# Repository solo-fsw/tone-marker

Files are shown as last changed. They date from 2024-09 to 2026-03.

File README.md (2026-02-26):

# Tone Marker

## Introduction
The purpose of the "Tone Marker" device is to translate high-frequency tones ($\ge$ 15 kHz) into Transistor-transistor Logic (TTL) markers. This allows any application with an audio output (e.g. virtual reality games, websites, cellphones) to send custom markers (values ranging from 0 up to 255) by embedding these marker tones in the audio output. The tones are filtered out and not audible to the participants.

Sending markers is necessary for synchronization of recorded data (e.g. BIOPAC measurements) with VR experiences, where hardware control is not possible. Marker tones are chosen in such a way that they are inaudible for the participant (through audio filtering).

The Tone Marker device is shown below. Note that the circles above the D7 to D0 label are LEDS indicating the currently active marker.

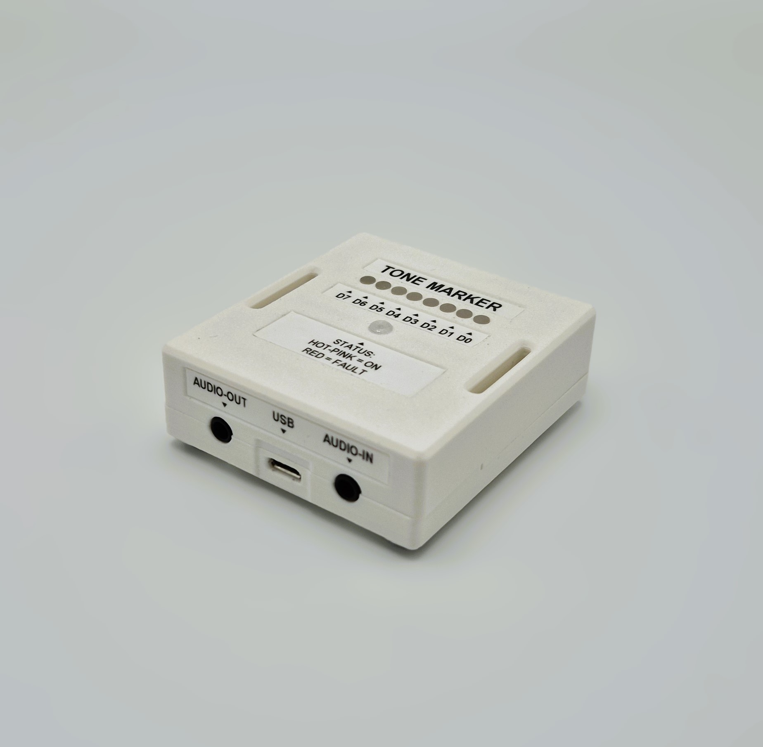
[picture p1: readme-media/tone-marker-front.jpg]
The Tone Marker device

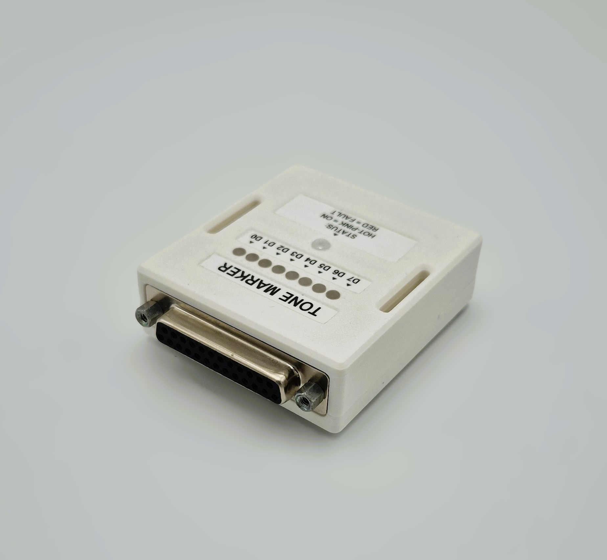
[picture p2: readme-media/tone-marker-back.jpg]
The Tone Marker device


## How to use it in your project?

1. Open your original audio or video file in editing software such as Audacity or Adobe Premiere Pro.
2. Download the audio files from the `media` folder. Both MP3 and WAV formats are available — choose the format that best fits your project requirements.
3. Create a new audio track in your editing software, and place the tone markers at the exact timestamps where you want to trigger events or synchronize actions.
4. Make sure that the marker track aligns correctly with the original audio.
5. Export the final project with both audio tracks included, so the tone markers can overlap with the original audio.

## How was Tone Marker device implemented?

### Setup
The Tone Marker device consists of a [Teensy 4.0](https://www.pjrc.com/store/teensy40.html) soldered to a custom PCB, which is based on the [Teensy Audio Shield](https://www.pjrc.com/store/teensy3_audio.html).
Power is provided through a Mini-USB connection to a dedicated power source (such as a powerbank). The audio input (from e.g. the VR glasses) is fed into the tone-marker, while simultaneously being fed directly into the marker destination (as a backup). Marker output is done through a Female DB25 connector, which is then connected to the required data recording device (e.g. BIOPAC, BIOSEMI).

An overview of the internal and external connections is shown below.

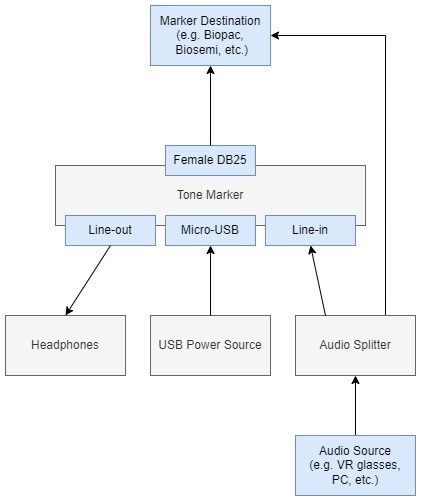
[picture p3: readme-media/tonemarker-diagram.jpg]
An overview of the connection in / to the Tone Marker device


> **NOTE**: Do not disconnect the Tone Marker device from power while it is still connected to a powered marker destination (e.g. a BIOPAC that is turned on). This may cause the Tone Marker device to enter a state where it attempts to power itself by drawing power from the marker destination, which may cause damage to the Teensy or the marker destination device. In this undesired state, the Tone Marker device's status LED may glow red instead of hot-pink.

### Communication protocol

The device expects tones (or combinations of tones) of specific frequencies. The device is currently uses an encoding system with a signal line and two data lines. The signal line makes the device enter listening mode. In listening mode the device receives a bitstring by interpreting the other two frequencies as either 0's (LOW) or 1's (high).

Frequencies are detected by the Goertzel algorithm, and are therefore optimized for their respective Goertzel bin. This is done for the Goertzel algorithm using 150 clock cycles and a sampling frequency of 44100, resulting in the following frequencies:

- **Signal frequency**: 15288.0 Hz
- **Data LOW frequency**: 15582.0 Hz
- **Data HIGH frequency**: 15876.0 Hz

### Delay

Due to time needed for communication and calculation of markers, there is a delay between the onset of the marker tones and the detection of a marker by a marker recipient (such as a Biopac). This delay is approximately $1668$ ms, with a standard deviation of $5.66$ ms.

## Known Issues

### Transient Marker Values
It was noticed that when measuring the marker outputs at 25 kHz using a BIOPAC, approximately 24 of 344 markers showed intermediate values when setting all bits to their ON state (255). When measuring at 2 kHz, the same problem occurred only once (1 / 344). In all cases, the intermediate values had a duration of only a single sample.

As such, it is vitally important to find and remove any such intermediate values before analyzing the data. Please not that the [PhysioData Toolbox](https://physiodatatoolbox.leidenuniv.nl/) automatically corrects for this by removing single-sample markers.

Note, it was not ruled out that this issue was (partly) caused by the BIOPAC's possibly non-simultaneous sampling of the digital input ports.

### Single-Register Patch
The current design spreads the marker IO pins across multiple port registers on the Teensy. A possible fix would be to redesigned the PCB in such a way that it makes use of a single port register, allowing faster bit setting. This may be accomplished using the pins mentioned below, since they are not used by the teensy audio shield, and can all be controlled by changing the GPIO6 register.

| Pin number 	| GPIO6 register index 	|
|------------	|----------------------	|
| 01         	| 02                   	|
| 00         	| 03                   	|
| 24         	| 12                   	|
| 14         	| 18                   	|
| 17         	| 22                   	|
| 16         	| 23                   	|
| 22         	| 24                   	|
| 26         	| 30                   	|

This single-register design was tested and still resulted in 2 out of 360 marker having intermediate values when measured using a BIOPAC at 25 kHz.

### Power supply
Currently, the device enters an undefined state while being connected to the powered BIOPAC without being powered by the micro-USB connector. This is due to the BIOPAC's pull-up resistors and could possibly damage the Teensy. Having the Tone Marker device off and connected to a powered BIOPAC should always be avoided.

## Notes

### Power supply

Some USB power adapters have some noise, which is then audible in the audio signal. In order to avoid this, the usage of a powerbank for powering the Tone Marker device is recommended.

### Volume

Different values of input audio volume might affect Tone Marker performance in different ways. The currently recommended volume level is 65% (on a windows PC) or 80% (on VR glasses).

Furthermore, VR glasses seem to have a lower volume output, so heightening the gain of the marker soundfiles is recommended. Marker functionality can be monitored by checking the green LEDs.

### Additional information / sources

- [Information on the Teensy 4.0 audioshield](https://forum.pjrc.com/index.php?threads/available-teensy-4-0-pins-when-audio-shield-d-attached.58331/)
- [Information on available Teensy pins while the audioshield is connected (and register mappings)](https://github.com/luni64/TeensyTimerTool/wiki/Avoid-PWM-timer-clashes)
- [Teensy pin-register forum thread](https://forum.pjrc.com/index.php?threads/teensy-4-1-digital-i-o-pin-map.64226/)
- [Using Teensy GPIO registers](https://forum.pjrc.com/index.php?threads/tutorial-on-digital-i-o-atmega-pin-port-ddr-d-b-registers-vs-arm-gpio_pdir-_pdor.17532/)
- [DigitalRead, DigitalWrite, DigitalWriteFast speeds](https://forum.pjrc.com/index.php?threads/speed-of-digitalread-and-digitalwrite-with-teensy3-0.24573/)
- [Additional explanation on registers](https://forum.pjrc.com/index.php?threads/unclear-on-how-to-use-ddrx-and-portx-teensy-3-2.53950/)
- [Goertzel Algorithm](https://courses.cs.washington.edu/courses/cse466/11au/resources/GoertzelAlgorithmEETimes.pdf)
- [Changing soundfile audio volume in python](https://stackoverflow.com/questions/43679631/python-how-to-change-audio-volume)

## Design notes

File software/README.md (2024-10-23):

# Software
This directory contains arduino software, that runs on the Teensy-based device, and python code, that is used to generate the marker tones.

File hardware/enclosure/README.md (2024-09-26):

# Enclosure #
Enclosure printed from PLA, see 3mf file.

Parts:
 - Bit LEDs light pipes: [LFB025CTP VCC](https://nl.rs-online.com/web/p/led-light-pipes/1371421).
 - Jackscrews: [RS PRO Screw Lock For Use With D Connector](https://nl.rs-online.com/web/p/d-sub-connector-accessories/0814039).
 - Threaded inserts: [RS PRO, M3 Brass Threaded Insert](https://nl.rs-online.com/web/p/threaded-inserts/0278534?gb=s)

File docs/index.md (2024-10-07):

# Tone Marker Test

## Standard encoding testfile

https://github.com/user-attachments/assets/777e4f00-1f3a-4553-8680-ae20917f563c

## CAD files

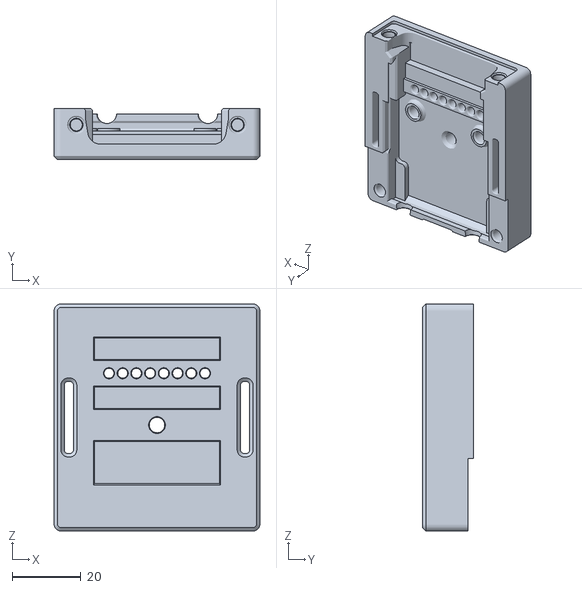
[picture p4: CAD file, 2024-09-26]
hardware/enclosure/Tone Marker v2 v26_Tone Marker v2 v26_Base_1_Body2.stl
60.0 x 15.0 x 66.2

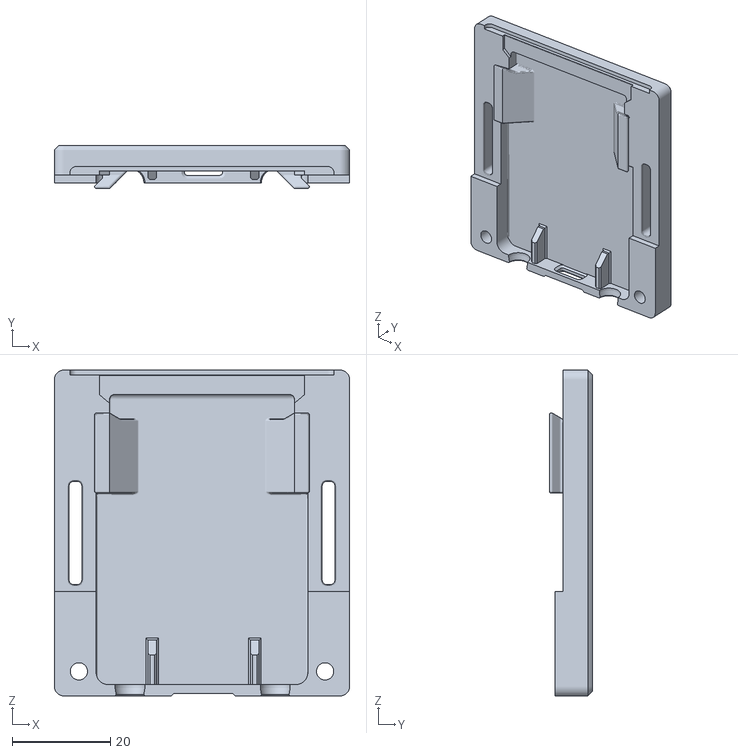
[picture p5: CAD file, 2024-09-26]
hardware/enclosure/Tone Marker v2 v26_Tone Marker v2 v26_Lid_1_Body1.stl
60.0 x 8.82 x 66.2

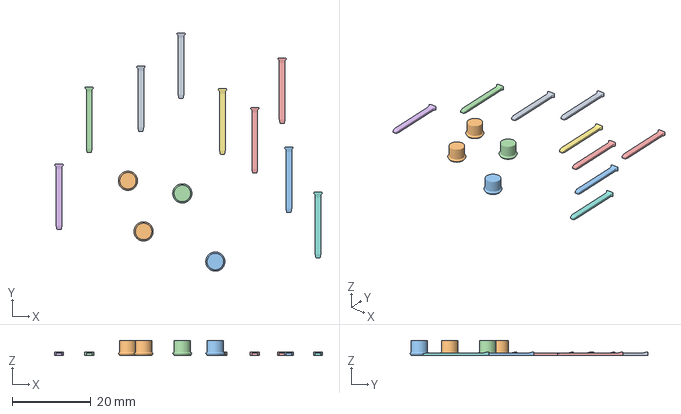
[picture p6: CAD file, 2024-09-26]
hardware/enclosure/LightPipes.3mf
68.1 x 60.6 x 3.87 mm
Body1.stl x 9
Component32.stl x 4

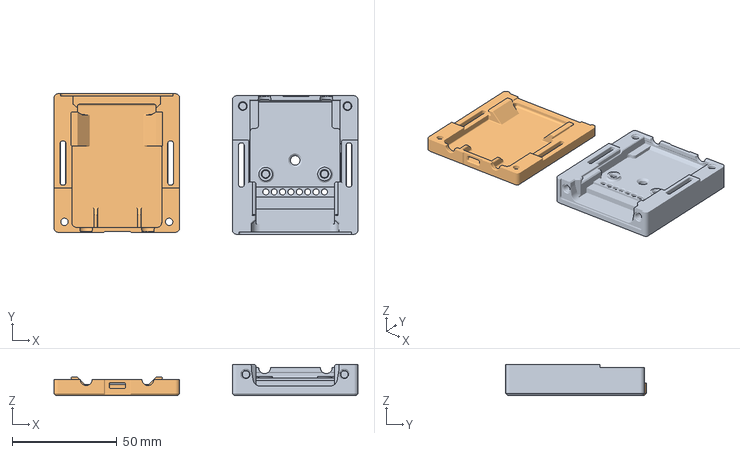
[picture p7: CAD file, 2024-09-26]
hardware/enclosure/Tone Marker.3mf
145.2 x 67.1 x 15.0 mm
Tone Marker v2 v26_Tone Marker v2 v26_Base_1_Body2.stl
Tone Marker v2 v26_Tone Marker v2 v26_Lid_1_Body1.stl

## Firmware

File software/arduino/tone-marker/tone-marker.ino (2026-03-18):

#include <Audio.h>
#include <Wire.h>
#include <SPI.h>
#include <SerialFlash.h>
#include <FastLED.h>

#define REQUIREMENTS_FOLLOWED false

#define DATA_PIN 17
#define N_LEDS 1
#define STRIPS 1
#define N_BITS 3
#define N_UNUSED_BITS 5

// Tool: https://www.pjrc.com/teensy/gui/

// GUItool: begin automatically generated code
AudioInputI2S i2s1;                  //xy=101,321
AudioFilterBiquad filterMarker;      //xy=346,417
AudioMixer4 mixerLeft;               //xy=348,268
AudioMixer4 mixerRight;              //xy=348,348
AudioMixer4 mixerMarker;             //xy=572,436
AudioFilterBiquad filterRight;       //xy=580,347
AudioFilterBiquad filterLeft;        //xy=584,268
AudioOutputI2S i2s2;                 //xy=781,307
AudioFilterBiquad filterBand1;       //xy=946,493
AudioFilterBiquad filterBand2;       //xy=949,544
AudioFilterBiquad filterBand3;       //xy=949,595
AudioMixer4 mixerMarker1;            //xy=1261,409
AudioMixer4 mixerMarker2;            //xy=1265,497
AudioMixer4 mixerMarker3;            //xy=1273,584
AudioAnalyzeToneDetect toneMarker1;  //xy=1506,410
AudioAnalyzeToneDetect toneMarker2;  //xy=1510,498
AudioAnalyzeToneDetect toneMarker3;  //xy=1512,584
AudioConnection patchCord1(i2s1, 0, mixerLeft, 0);
AudioConnection patchCord2(i2s1, 1, filterMarker, 0);
AudioConnection patchCord3(i2s1, 1, mixerRight, 0);
AudioConnection patchCord4(filterMarker, 0, mixerMarker, 0);
AudioConnection patchCord5(mixerLeft, filterLeft);
AudioConnection patchCord6(mixerRight, filterRight);
AudioConnection patchCord7(mixerMarker, filterBand1);
AudioConnection patchCord8(mixerMarker, filterBand2);
AudioConnection patchCord9(mixerMarker, filterBand3);
AudioConnection patchCord10(filterRight, 0, i2s2, 1);
AudioConnection patchCord11(filterLeft, 0, i2s2, 0);
AudioConnection patchCord12(filterBand1, 0, mixerMarker1, 0);
AudioConnection patchCord13(filterBand2, 0, mixerMarker2, 0);
AudioConnection patchCord14(filterBand3, 0, mixerMarker3, 0);
AudioConnection patchCord15(mixerMarker1, toneMarker1);
AudioConnection patchCord16(mixerMarker2, toneMarker2);
AudioConnection patchCord17(mixerMarker3, toneMarker3);
AudioControlSGTL5000 sgtl5000_1;  //xy=858,202
// GUItool: end automatically generated code

// For optimal detection, the target frequencies should be integer multiples of the sampling rate divided by the amount of sampled cycles
float SAMPELING_FREQUENCY = 44100;  // Hz
float GOERTZEL_CYCLES = 150;
float FREQUENCY_MULTIPLES = SAMPELING_FREQUENCY / GOERTZEL_CYCLES;
float STARTING_MULTIPLE = 52.0;  // 52 --> 15288.0

struct BitState {
  bool goertzelState;
  bool debounceState;
  elapsedMillis debounceTime;
  bool markerState;
  elapsedMillis markerTime;
  int bitIdx;
  int pinNr;
  float frequency;
  float gain;
  float certainty;
  AudioFilterBiquad *bandFilter;
  AudioMixer4 *amplifier;
  AudioAnalyzeToneDetect *freqFilter;
};

BitState bits[N_BITS] = {
  { 0, 0, 0, 0, 0, 0, 0, (STARTING_MULTIPLE + 0) * FREQUENCY_MULTIPLES, 4.0, 0.5, &filterBand1, &mixerMarker1, &toneMarker1 },
  { 0, 0, 0, 0, 0, 1, 1, (STARTING_MULTIPLE + 1) * FREQUENCY_MULTIPLES, 4.0, 0.4, &filterBand2, &mixerMarker2, &toneMarker2 },
  { 0, 0, 0, 0, 0, 2, 2, (STARTING_MULTIPLE + 2) * FREQUENCY_MULTIPLES, 6.0, 0.4, &filterBand3, &mixerMarker3, &toneMarker3 },
};

int pins[8] = { 0, 1, 2, 3, 4, 5, 6, 9 };
int unusedMarkerPins[N_UNUSED_BITS] = { 3, 4, 5, 6, 9 };
int markerValues[8] = { 0, 0, 0, 0, 0, 0, 0, 0 };
uint8_t virtualRegister = 0x00;

const int SIGNAL_TONE = 0;
const int DATA_LOW = 1;
const int DATA_HIGH = 2;
elapsedMillis markerClock = 0;

// Initialize led strip (status led)
CRGB leds[N_LEDS * STRIPS];
CRGB::HTMLColorCode ON = CRGB::HotPink;
CRGB::HTMLColorCode SENDING = CRGB::DarkGreen;
CRGB::HTMLColorCode FAULT = CRGB::DarkRed;

// Declare global variables and constants
const float FILTER_FREQ = 14000.0;
const float FILTER_FREQ_LP = 12000.0;
const unsigned int DEBOUNCE_DELAY = 50;
const unsigned int TONE_DETECTION_DURATION = 600;

float mixerLeftGain = 0.5;
float mixerRightGain = 0.5;
float mixerMarkerGain = 2.4;

float lowpassQualityLeft1 = 5.0;
float lowpassQualityRight1 = 5.0;
float highpassQuality = 8.0;
float bandFilterQuality = 8.0;

void setup() {
  // Start serial connection
  Serial.begin(9600);

  // Initialize audio buffer and start main audio controller
  AudioMemory(20);
  sgtl5000_1.enable();
  sgtl5000_1.volume(0.5);
  sgtl5000_1.inputSelect(AUDIO_INPUT_LINEIN);

  // Initialize lowpass filters
  // filterLeft.setLowpass(0, FILTER_FREQ, lowpassQualityLeft1);
  // filterRight.setLowpass(0, FILTER_FREQ, lowpassQualityRight1);

  // Linkwitz-Riley filter, 48 dB/octave
  filterLeft.setLowpass(0, FILTER_FREQ_LP, 0.54);
  filterLeft.setLowpass(1, FILTER_FREQ_LP, 1.3);
  filterLeft.setLowpass(2, FILTER_FREQ_LP, 0.54);
  filterLeft.setLowpass(3, FILTER_FREQ_LP, 1.3);

  filterRight.setLowpass(0, FILTER_FREQ_LP, 0.54);
  filterRight.setLowpass(1, FILTER_FREQ_LP, 1.3);
  filterRight.setLowpass(2, FILTER_FREQ_LP, 0.54);
  filterRight.setLowpass(3, FILTER_FREQ_LP, 1.3);

  filterLeft.setNotch(1, bits[SIGNAL_TONE].frequency);
  filterRight.setNotch(1, bits[SIGNAL_TONE].frequency);

  filterLeft.setNotch(2, bits[DATA_LOW].frequency);
  filterRight.setNotch(2, bits[DATA_LOW].frequency);

  filterLeft.setNotch(3, bits[DATA_HIGH].frequency);
  filterRight.setNotch(3, bits[DATA_HIGH].frequency);

  // filterLeft.setLowpass(1, FILTER_FREQ, lowpassQualityLeft2);
  // filterRight.setLowpass(1, FILTER_FREQ, lowpassQualityRight2);

  // Initialize highpass filter
  filterMarker.setHighpass(0, FILTER_FREQ, highpassQuality);

  // Set gains
  mixerLeft.gain(0, mixerLeftGain);      // lowpass
  mixerRight.gain(0, mixerRightGain);    // lowpass
  mixerMarker.gain(0, mixerMarkerGain);  // highpass

  // Initialize led strip (status led)
  FastLED.addLeds<STRIPS, WS2812B, DATA_PIN, GRB>(leds, N_LEDS);
  FastLED.setBrightness(40);
  FastLED.setMaxPowerInVoltsAndMilliamps(5, 500);

  // Set status led to pink
  FastLED.clear();
  leds[0] = ON;
  FastLED.show();

  // Initialize marker pins and corresponding frequency filters
  for (int idx = 0; idx < N_BITS; idx++) {
    pinMode(bits[idx].pinNr, OUTPUT);
    bits[idx].bandFilter->setBandpass(0, bits[idx].frequency, bandFilterQuality);
    bits[idx].amplifier->gain(0, bits[idx].gain);
    bits[idx].freqFilter->frequency(bits[idx].frequency, GOERTZEL_CYCLES);
  }

  for (int idx = 0; idx < N_UNUSED_BITS; idx++) {
    pinMode(unusedMarkerPins[idx], OUTPUT);
  }
};

// Sets marker bits according to the status information in the (virtual) register
void setMarkerBits(uint8_t virtualRegister) {
  if (REQUIREMENTS_FOLLOWED) {

  } else {
    for (int idx = 0; idx < 8; idx++) {
      digitalWriteFast(pins[idx], ((virtualRegister >> idx) & 0x01));
    }
  }
};

void checkFreqs() {
  for (int idx = 0; idx < N_BITS; idx++) {
    bits[idx].goertzelState = bits[idx].freqFilter->read() > bits[idx].certainty;
    if (bits[idx].goertzelState == bits[idx].debounceState) {
      bits[idx].debounceTime = 0;
    } else if (bits[idx].debounceTime > DEBOUNCE_DELAY) {
      bits[idx].debounceState = bits[idx].goertzelState;
      bits[idx].debounceTime = 0;
      bits[idx].markerTime = 0;
    }
  }
};

void loop() {
  checkFreqs();
  if (bits[SIGNAL_TONE].debounceState && markerClock > 2000) {
    markerClock = 0;
    for (unsigned int idx = 0; idx < 8; idx++) {
      int highCount = 0;
      int lowCount = 0;
      while (markerClock < (200 * (idx + 1))) {
        checkFreqs();
        if (bits[DATA_LOW].debounceState) {
          lowCount++;
        } else if (bits[DATA_HIGH].debounceState) {
          highCount++;
        }
      }
      if (highCount >= lowCount) {
        markerValues[idx] = 1;
      } else {
        markerValues[idx] = 0;
      }
    }
    for (int i = 0; i < 8; i++) {
      virtualRegister = virtualRegister | (markerValues[i] << i);
      Serial.print(markerValues[7 - i]);
    }
    Serial.println("");
    setMarkerBits(virtualRegister);
    delay(500);
    virtualRegister = 0x00;
    setMarkerBits(virtualRegister);
  }
};

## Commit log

2024-06-19 Tone Marker Device (#1)
    * init commit
    * updated log and readme
    * Sound marker communication protocol code
    * Added marker processing, updated log
    * Working character recognition
    * Overflow clause
    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
    [Tone Enclosure Bottom.3mf, Tone Enclosure Top.3mf]
2024-07-02 Added bandpass filters and amplification mixers
2024-09-18 added hardware files
    [LightPipes.3mf, Tone Enclosure Bottom.3mf, Tone Enclosure Top.3mf, Tone Marker v2 v26_Tone Marker v2 v26_Base_1_Body2.stl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]
2024-09-26 Led cleanup
2026-03-18 Changed LP filter to Linkwitz-Riley
2026-06-01 Ignore Arduino tone-marker build directory
